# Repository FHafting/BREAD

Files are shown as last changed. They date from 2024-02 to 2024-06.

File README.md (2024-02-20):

# BREAD
This project is fully documented in the paper: Shane Oberloier, Nicholas G. Whisman, Finn Hafting, Joshua M. Pearce, Open Source Framework for a Broadly Expandable and Reconfigurable Data Acquisition and Automation Device (BREAD), ''HardwareX'', 2023, e00467, https://doi.org/10.1016/j.ohx.2023.e00467.

All case designs can be found on Onshape: https://cad.onshape.com/documents/f4c13a5c0b1f8d88ed1f5752/w/29d0c0346ddaeb06e16ff42f/e/1077373224ada363d171e3fe?renderMode=0&uiState=65d3aad45b82c32cb51ae4c9

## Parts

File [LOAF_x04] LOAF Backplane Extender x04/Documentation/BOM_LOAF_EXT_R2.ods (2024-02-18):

References | Value | Footprint | Quantity | URL
J2, J3, J4, J5 | Conn_01x10_Male | BREAD 10-Pin Connector | 4 | https://www.digikey.ca/en/products/detail/amphenol-cs-fci/10129378-910002BLF/7915958
J1 | 10129379-910002BLF | 1x10 RA Male Header 2.54mm Pitch | 1 | https://www.digikey.ca/en/products/detail/amphenol-cs-fci/10129379-910002BLF/7916010
J6 | PPPC101LGBN-RC | PinSocket_1x10_P2.54mm_Horizontal | 1 | https://www.digikey.ca/en/products/detail/sullins-connector-solutions/PPTC101LGBN-RC/775904
J7 | Barrel_Jack | BarrelJack_CUI_PJ-063AH_Horizontal | 1 | https://www.digikey.ca/en/products/detail/cui-devices/pj-063ah/2161208

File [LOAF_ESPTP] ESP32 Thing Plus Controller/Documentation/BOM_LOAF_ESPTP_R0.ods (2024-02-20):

References | Value | Footprint | Quantity | URL | Alternate
C1, C3, C4 | 22uF | C_1206_3216Metric | 3 | https://www.digikey.ca/en/products/detail/samsung-electro-mechanics/CL31A226KAHNNNE/3888705
C2 | 100nF | C_1206_3216Metric | 1 | https://www.digikey.ca/en/products/detail/samsung-electro-mechanics/CL31B104KBCNNNC/3886675
R1, R2, R3, R4, R5, R6, R7 | 10k | R_0603_1608Metric | 7 | https://www.digikey.ca/en/products/detail/stackpole-electronics-inc/RMCF0603FT10K0/1761235
R9, R11 | 4.7k | R_0603_1608Metric | 2 | https://www.digikey.ca/en/products/detail/stackpole-electronics-inc/RMCF0603FT4K70/1760998
R10, R12 | 2.2k | R_0603_1608Metric | 2 | https://www.digikey.ca/en/products/detail/yageo/RC0603JR-132K2L/14286397
R8 | 200k | R_0603_1608Metric | 1 | https://www.digikey.ca/en/products/detail/stackpole-electronics-inc/RMCF0603FT200K/1760715
L1 | 4.7uH | L_1210_3225Metric | 1 | https://www.digikey.ca/en/products/detail/tdk-corporation/BCL322520RT-4R7M-D/15849704
U1 | LTC4311ISC6-TRMPBF | SOT-363_SC-70-6 | 1 | https://www.digikey.ca/en/products/detail/analog-devices-inc/LTC4311ISC6-TRMPBF/1814493
U2 | AP63205WU-7 | TSOT-23-6 | 1 | https://www.digikey.ca/en/products/detail/diodes-incorporated/AP63205WU-7/9858424
U3 | PCA9306 | SSOP-8_2.95x2.8mm_P0.65mm | 1 | https://www.digikey.ca/en/products/detail/texas-instruments/PCA9306DCUR/768359
Q1, Q2, Q3 | BSS138 | SOT-23 | 3 | https://www.digikey.ca/en/products/detail/diodes-incorporated/BSS138-7-F/717843?productid=717843&gad_source=1
HS1 | Heatsink_Pad (optional) | Thermal Pad | 1 | https://www.digikey.ca/en/products/detail/assmann-wsw-components/V2017B/3511410
J2 | THING_PLUS_LOGICAL | ESP_THING_PLUS | 1 | https://www.sparkfun.com/products/20168 | https://www.digikey.ca/en/products/detail/sparkfun-electronics/WRL-20168/16688100
J6 | PPTC101LGBN-RC | PinSocket_1x10_P2.54mm_Horizontal | 1 | https://www.digikey.ca/en/products/detail/sullins-connector-solutions/PPTC101LGBN-RC/775904

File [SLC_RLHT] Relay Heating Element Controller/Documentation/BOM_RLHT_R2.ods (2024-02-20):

References | Value | Footprint | Quantity | URL
C1, C3, C4 | 22uF | C_1206_3216Metric | 3 | https://www.digikey.ca/en/products/detail/samsung-electro-mechanics/CL31A226KAHNNNE/3888705
C5, C6 | 0.01 uF | C_1206_3216Metric | 2 | https://www.digikey.ca/en/products/detail/walsin-technology-corporation/1206B103J500CT/9355096
C2 | 100nF | C_1206_3216Metric | 1 | https://www.digikey.ca/en/products/detail/samsung-electro-mechanics/CL31B104KBCNNNC/3886675
L1 | 4.7uH | L_1210_3225Metric | 1 | https://www.digikey.ca/en/products/detail/tdk-corporation/BCL322520RT-4R7M-D/15849704
D2, D3 | General_Purpose_Diode | D_DO-35_SOD27_P7.62mm_Horizontal | 2 | https://www.digikey.ca/en/products/detail/onsemi/1N914B/978757
D1 | WS2812B_5050 | WS2812-5050-4PIN | 1 | https://www.digikey.ca/en/products/detail/sparkfun-electronics/COM-16347/11630204
U2, U5 | TCMT1100 | SOP-4_4.4x2.6mm_P1.27mm | 2 | https://www.digikey.ca/en/products/detail/vishay-semiconductor-opto-division/TCMT1100/1738630
U3, U4 | MAX6675ISA+ | SOIC127P600X175-8N | 2 | https://www.digikey.ca/en/products/detail/maxim-integrated/MAX6675ISA/1513517
U1 | AP63205WU-7 | TSOT-23-6 | 1 | https://www.digikey.ca/en/products/detail/diodes-incorporated/AP63205WU-7/9858424
F1, F2 | 10A | Glass Fuse Clip x2 (5x20MM) | 4 | https://www.digikey.ca/en/products/detail/bel-fuse-inc/FC-211-BRIGHT-TIN/622587
A1 | Arduino_Nano_v3.x | Arduino_Nano | 1 | https://www.amazon.ca/ELEGOO-Arduino-ATmega328P-Without-Compatible/dp/B0713XK923
FB1, FB2, FB3, FB4 | Ferrite_Bead_Small | R_1206_3216Metric | 4 | https://www.digikey.ca/en/products/detail/w%C3%BCrth-elektronik/74279215/1639033
K1, K2 | G5Q-1 | Relay_SPDT_Omron-G5Q-1 | 2 | https://www.digikey.ca/en/products/detail/omron-electronics-inc-emc-div/G5Q-14-DC12/355243
HS1 | Heatsink_Pad (optional) | Thermal Pad | 1 | https://www.digikey.ca/en/products/detail/assmann-wsw-components/V2017B/3511410
J4 | Term_PressFit_Phoenix_Contact | Term_PressFit_3.5mm_H_ENDCAP_PC | 1 (4x) | https://www.digikey.ca/en/products/detail/phoenix-contact/1990753/2527254
J3, J11, J12 | Term_PressFit_Phoenix_Contact | Term_PressFit_3.5mm_H_PC
J1 | Conn_01x10_Female | PinSocket_1x10_P2.54mm_Horizontal | 1 | https://www.digikey.ca/en/products/detail/sullins-connector-solutions/PPTC101LGBN-RC/775904
J2 | I2C_01x04 | JST_SH_SM04B-SRSS-TB_1x04-1MP_P1.00mm_Horizontal | 1 | https://www.digikey.ca/en/products/detail/jst-sales-america-inc/SM04B-SRSS-TB/926710
J6, J7, J8, J9, J10, J13, J14, J15, J16, J17, J18 | Term_PressFit_Phoenix_Contact | Term_PressFit_5mm_H_PC_HVRELAY | 2 (6x) | https://www.digikey.ca/en/products/detail/phoenix-contact/1991011/2527265
J5 | Term_PressFit_Phoenix_Contact | Term_PressFit_5mm_H_ENDCAP_PC_HVRELAY
 | 10A | Glass Fuse 5x20mm | 2 | https://www.digikey.ca/en/products/detail/bel-fuse-inc/5ST-10-R/1009028

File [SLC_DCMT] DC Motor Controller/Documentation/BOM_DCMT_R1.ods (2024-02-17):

References | Value | Footprint | Quantity | URL
C6, C8, C9, C10, C11, C12 | 10 nF | C_1206_3216Metric_Pad1.33x1.80mm_HandSolder | 6 | https://www.digikey.ca/en/products/detail/walsin-technology-corporation/1206B103J500CT/9355096
C1, C5, C7 | 22uF | C_1206_3216Metric | 3 | https://www.digikey.ca/en/products/detail/samsung-electro-mechanics/CL31A226KAHNNNE/3888705
C2, C3 | 10uF_t | C_1206_3216Metric | 2 | https://www.digikey.ca/en/products/detail/yageo/cc1206kkx5r8bb106/2833631
C4 | 100nF | C_1206_3216Metric | 1 | https://www.digikey.ca/en/products/detail/samsung-electro-mechanics/CL31B104KBCNNNC/3886675
R1, R2 | 4.42 k | R_1206_3216Metric_Pad1.30x1.75mm_HandSolder | 2 | https://www.digikey.ca/en/products/detail/yageo/RC1206FR-074K42L/728878
L1 | 4.7uH | L_1210_3225Metric | 1 | https://www.digikey.ca/en/products/detail/tdk-corporation/BCL322520RT-4R7M-D/15849704
D2 | WS2812B_5050 | WS2812-5050-4PIN | 1 | https://www.digikey.ca/en/products/detail/sparkfun-electronics/COM-16347/11630204
U1, U3 | LMD18200 | TO-220-11_P3.4x5.08mm_StaggerOdd_Lead4.85mm_Vertical | 2 | https://www.digikey.ca/en/products/detail/texas-instruments/LMD18200T/3701191
U2 | AP63205WU-7 | TSOT-23-6 | 1 | https://www.digikey.ca/en/products/detail/diodes-incorporated/AP63205WU-7/9858424
SW1, SW2 | SW_SPDT | L102011MS02Q | 2 | https://www.digikey.ca/en/products/detail/c-k/L102011MS02Q/484143
A1 | Arduino_Nano_v3.x | Arduino_Nano | 1 | https://www.amazon.ca/ELEGOO-Arduino-ATmega328P-Without-Compatible/dp/B0713XK923
HS1 | Heatsink_Pad (optional) | Thermal Pad | 1 | https://www.digikey.ca/en/products/detail/assmann-wsw-components/V2017B/3511410
J10, J11, J13, J15, J16, J17 | Term_PressFit_Phoenix_Contact | Term_PressFit_5mm_H_PC | 2 (4x) | https://www.digikey.ca/en/products/detail/phoenix-contact/1990999/3605138
J12, J14 | Term_PressFit_Phoenix_Contact | Term_PressFit_5mm_H_ENDCAP_PC
J2, J3, J4, J5, J7, J8, J9 | Term_PressFit_Phoenix_Contact | Term_PressFit_3.5mm_H_PC | 1 (8x) | https://www.digikey.ca/en/products/detail/phoenix-contact/1990795/3605145
J6 | Term_PressFit_Phoenix_Contact | Term_PressFit_3.5mm_H_ENDCAP_PC | 1
J1 | Conn_01x10_Female | PinSocket_1x10_P2.54mm_Horizontal | 1 | https://www.digikey.ca/en/products/detail/sullins-connector-solutions/PPTC101LGBN-RC/775904
J18 | I2C_01x04 | JST_SH_SM04B-SRSS-TB_1x04-1MP_P1.00mm_Horizontal | 1 | https://www.digikey.ca/en/products/detail/jst-sales-america-inc/SM04B-SRSS-TB/926710

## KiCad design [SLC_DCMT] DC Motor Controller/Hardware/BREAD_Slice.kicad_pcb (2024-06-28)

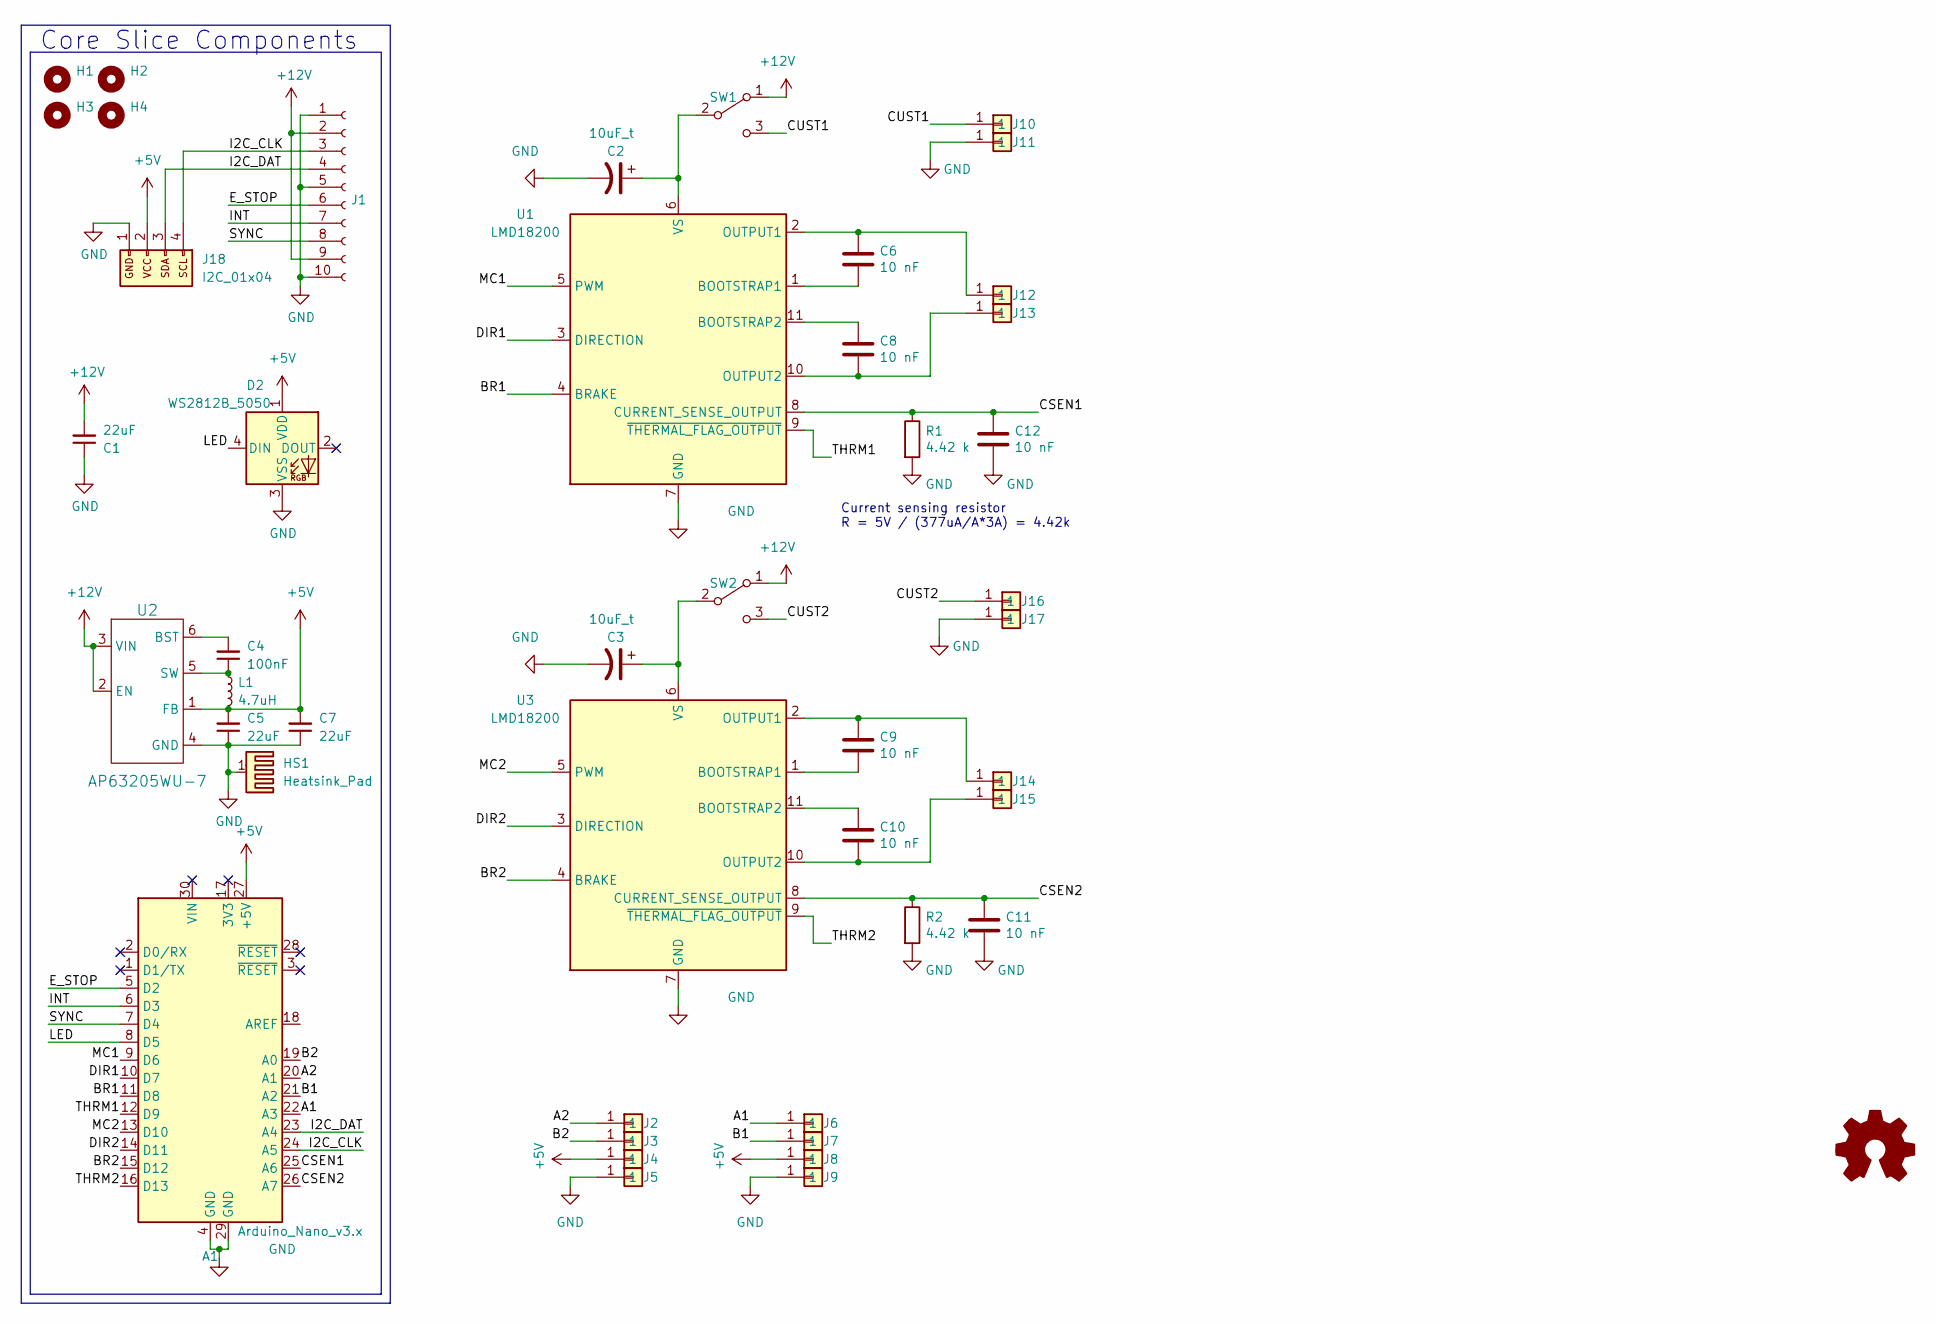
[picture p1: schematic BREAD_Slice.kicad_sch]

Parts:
A1: Arduino_Nano_v3.x; Arduino_Nano
C1, C5, C7: 22uF; C_1206_3216Metric
C2, C3: 10uF_t; C_1206_3216Metric; Part # T491C106K025AT
C4: 100nF; C_1206_3216Metric
C6, C8, C9, C10, C11, C12: 10 nF; C_1206_3216Metric_Pad1.33x1.80mm_HandSolder
D2: WS2812B_5050; WS2812-5050-4PIN
H1, H2, H3, H4: MountingHole; MountingHole_5mm
HS1: Heatsink_Pad; Thermal Pad
J1: Conn_01x10_Female; PinSocket_1x10_P2.54mm_Horizontal
J2, J3, J4, J5, J7, J8, J9: Term_PressFit_Phoenix_Contact; Term_PressFit_3.5mm_H_PC
J6: Term_PressFit_Phoenix_Contact; Term_PressFit_3.5mm_H_ENDCAP_PC
J10, J11, J13, J15, J16, J17: Term_PressFit_Phoenix_Contact; Term_PressFit_5mm_H_PC
J12, J14: Term_PressFit_Phoenix_Contact; Term_PressFit_5mm_H_ENDCAP_PC
J18: I2C_01x04; JST_SH_SM04B-SRSS-TB_1x04-1MP_P1.00mm_Horizontal
L1: 4.7uH; L_1210_3225Metric
Logo1: Logo_Open_Hardware_Small; OSHW-Symbol_6.7x6mm_SilkScreen
R1, R2: 4.42 k; R_1206_3216Metric_Pad1.30x1.75mm_HandSolder
SW1, SW2: SW_SPDT; L102011MS02Q
U1, U3: LMD18200; TO-220-11_P3.4x5.08mm_StaggerOdd_Lead4.85mm_Vertical
U2: AP63205WU-7; TSOT-23-6

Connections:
+5V: A1.27 (+5V), C5.2, C7.2, D2.1 (VDD), J4.1, J8.1, J18.2, L1.2, U2.1 (FB)
+12V: C1.2, J1.2, J1.9, SW1.1 (A), SW2.1 (A), U2.2 (EN), U2.3 (VIN)
/A1: A1.22 (A3), J6.1
/A2: A1.20 (A1), J2.1
/B1: A1.21 (A2), J7.1
/B2: A1.19 (A0), J3.1
/BR1: A1.11 (D8), U1.4 (BRAKE)
/BR2: A1.15 (D12), U3.4 (BRAKE)
/CSEN1: A1.25 (A6), C12.1, R1.1, U1.8 (CURRENT_SENSE_OUTPUT)
/CSEN2: A1.26 (A7), C11.1, R2.1, U3.8 (CURRENT_SENSE_OUTPUT)
/CUST1: J10.1, SW1.3 (C)
/CUST2: J16.1, SW2.3 (C)
/DIR1: A1.10 (D7), U1.3 (DIRECTION)
/DIR2: A1.14 (D11), U3.3 (DIRECTION)
/E_STOP: A1.5 (D2), J1.6
/I2C_CLK: A1.24 (A5), J1.3, J18.4
/I2C_DAT: A1.23 (A4), J1.4, J18.3
/INT: A1.6 (D3), J1.7
/LED: A1.8 (D5), D2.4 (DIN)
/MC1: A1.9 (D6), U1.5 (PWM)
/MC2: A1.13 (D10), U3.5 (PWM)
/SYNC: A1.7 (D4), J1.8
/THRM1: A1.12 (D9), U1.9 (~THERMAL_FLAG_OUTPUT)
/THRM2: A1.16 (D13), U3.9 (~THERMAL_FLAG_OUTPUT)
GND: A1.4 (GND), A1.29 (GND), C1.1, C2.2, C3.2, C5.1, C7.1, C11.2, C12.2, D2.3 (VSS), HS1.1, J1.1, J1.5, J1.10, J5.1, J9.1, J11.1, J17.1, J18.1, R1.2, R2.2, U1.7 (GND), U2.4 (GND), U3.7 (GND)
unnamed: C2.1, SW1.2 (B), U1.6 (VS)
unnamed: C3.1, SW2.2 (B), U3.6 (VS)
unnamed: C6.2, U1.1 (BOOTSTRAP1)
unnamed: C8.1, U1.11 (BOOTSTRAP2)
unnamed: C6.1, J12.1, U1.2 (OUTPUT1)
unnamed: C8.2, J13.1, U1.10 (OUTPUT2)
unnamed: C4.2, U2.6 (BST)
unnamed: C4.1, L1.1, U2.5 (SW)
unnamed: C9.2, U3.1 (BOOTSTRAP1)
unnamed: C10.1, U3.11 (BOOTSTRAP2)
unnamed: C9.1, J14.1, U3.2 (OUTPUT1)
unnamed: C10.2, J15.1, U3.10 (OUTPUT2)

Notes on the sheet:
Current sensing resistor R = 5V / (377uA/A*3A) = 4.42k
Core Slice Components

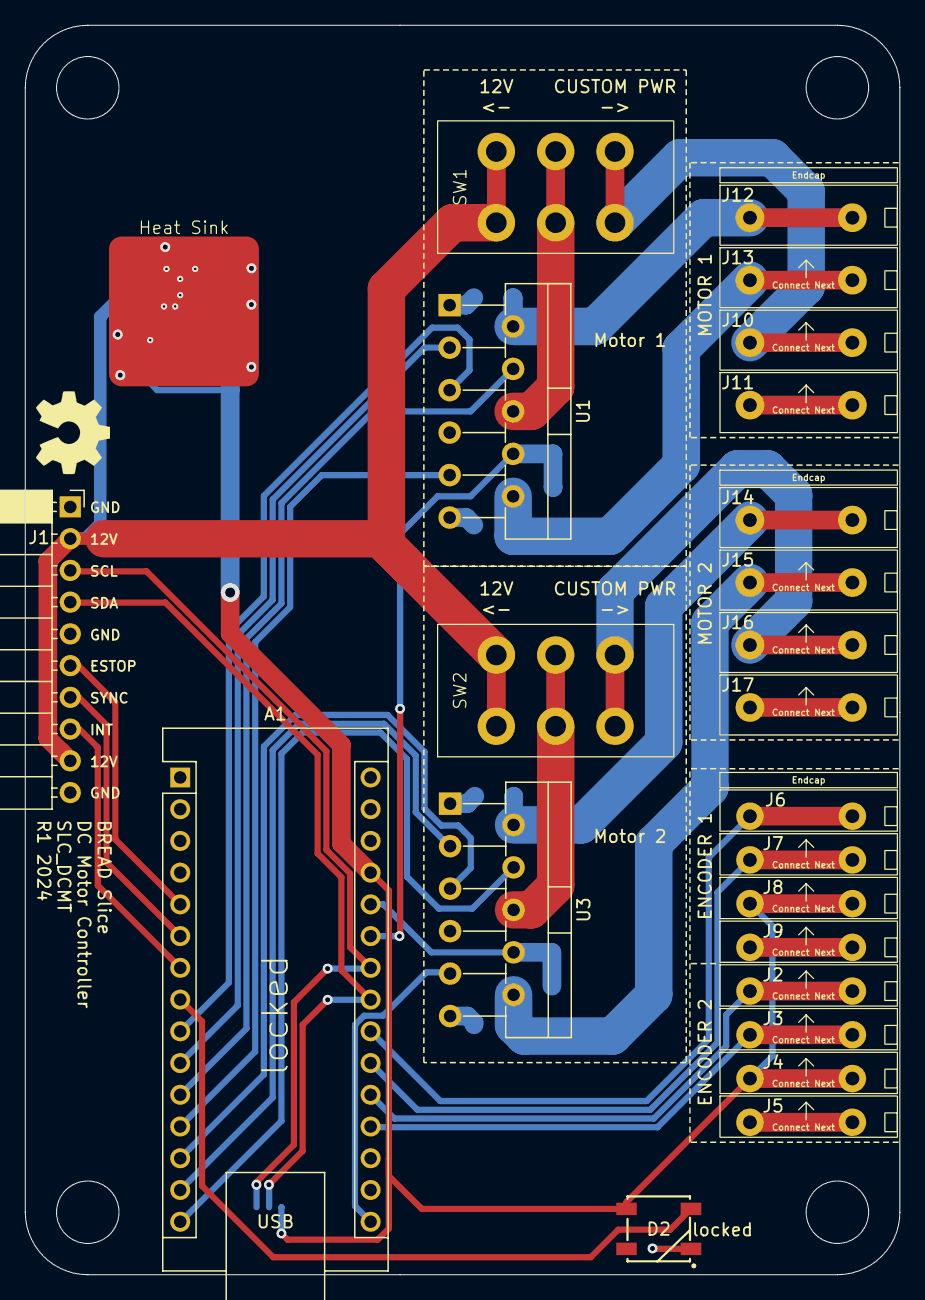
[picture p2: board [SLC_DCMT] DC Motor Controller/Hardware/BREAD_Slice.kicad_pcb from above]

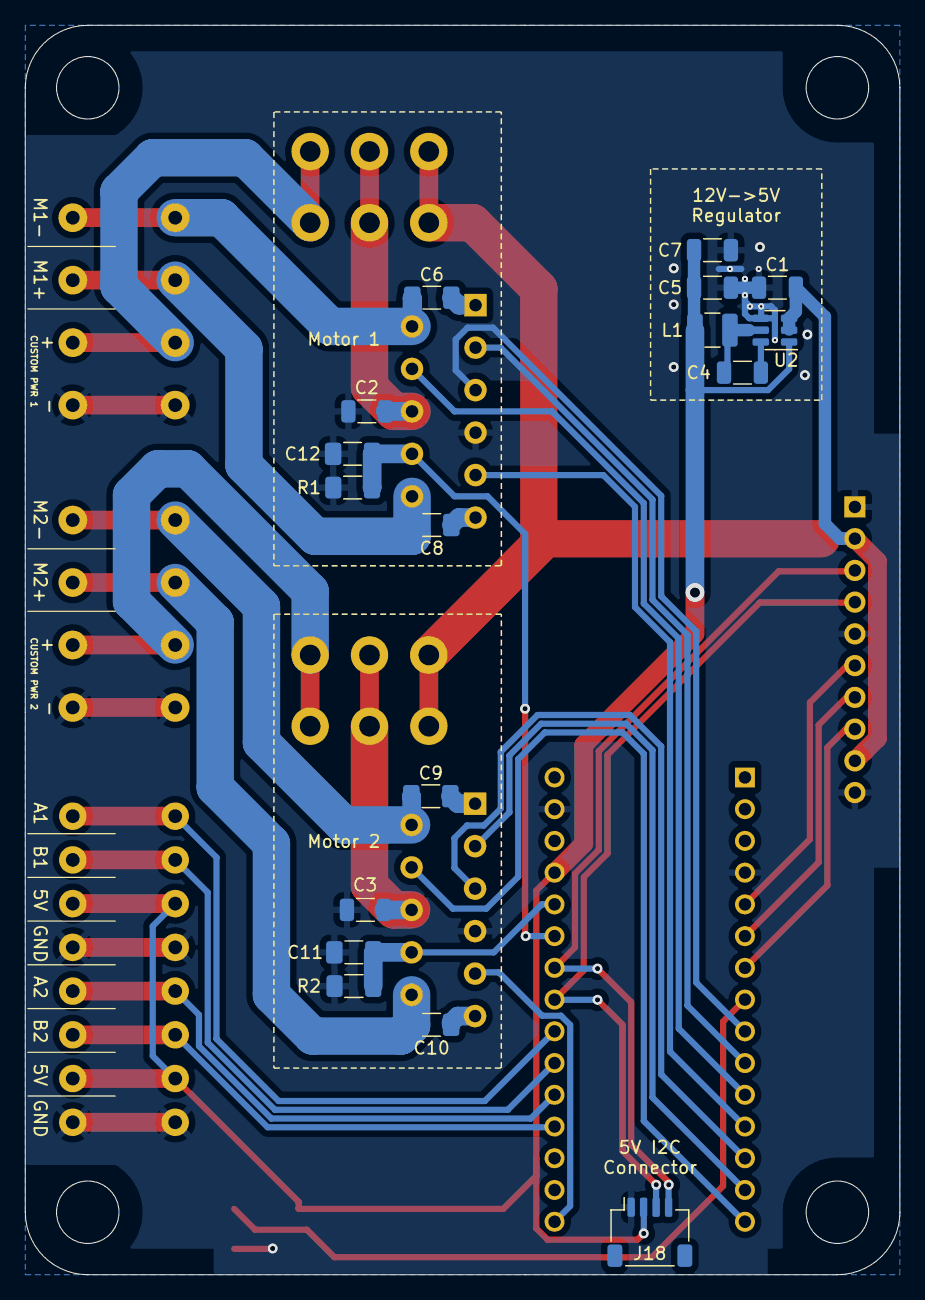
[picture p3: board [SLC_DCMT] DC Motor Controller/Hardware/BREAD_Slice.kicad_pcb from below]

Board: 2 copper layers, 70.0 x 100.0 mm, 46 parts (17 on the bottom side), 37 nets.

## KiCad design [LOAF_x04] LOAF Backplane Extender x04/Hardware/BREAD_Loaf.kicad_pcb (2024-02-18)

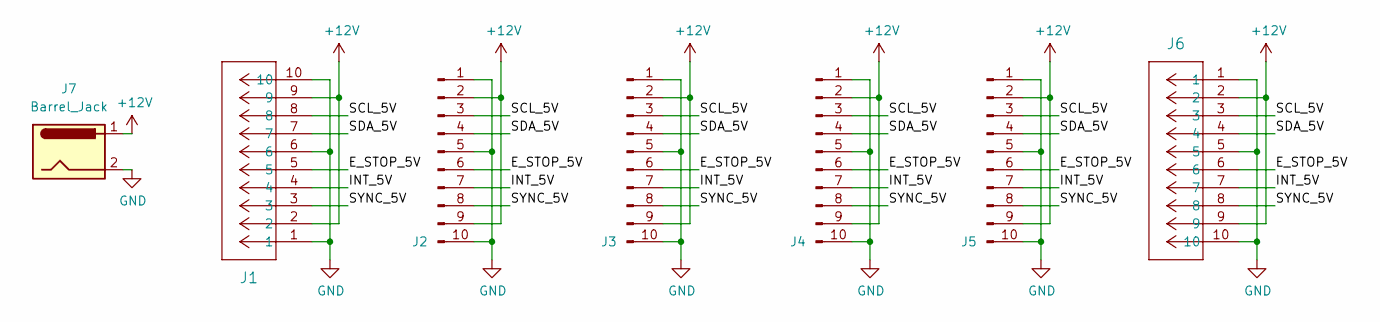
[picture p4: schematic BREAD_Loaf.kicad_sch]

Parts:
J1: PPPC101LGBN-RC; 1x10 RA Male Header 2.54mm Pitch
J2, J3, J4, J5: Conn_01x10_Male; BREAD 10-Pin Connector
J6: PPPC101LGBN-RC; PinSocket_1x10_P2.54mm_Horizontal
J7: Barrel_Jack; BarrelJack_CUI_PJ-063AH_Horizontal

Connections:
+12V: J1.2, J1.9, J2.2, J2.9, J3.2, J3.9, J4.2, J4.9, J5.2, J5.9, J6.2, J6.9, J7.1
/E_STOP_5V: J1.5, J2.6, J3.6, J4.6, J5.6, J6.6
/INT_5V: J1.4, J2.7, J3.7, J4.7, J5.7, J6.7
/SCL_5V: J1.8, J2.3, J3.3, J4.3, J5.3, J6.3
/SDA_5V: J1.7, J2.4, J3.4, J4.4, J5.4, J6.4
/SYNC_5V: J1.3, J2.8, J3.8, J4.8, J5.8, J6.8
GND: J1.1, J1.6, J1.10, J2.1, J2.5, J2.10, J3.1, J3.5, J3.10, J4.1, J4.5, J4.10, J5.1, J5.5, J5.10, J6.1, J6.5, J6.10, J7.2

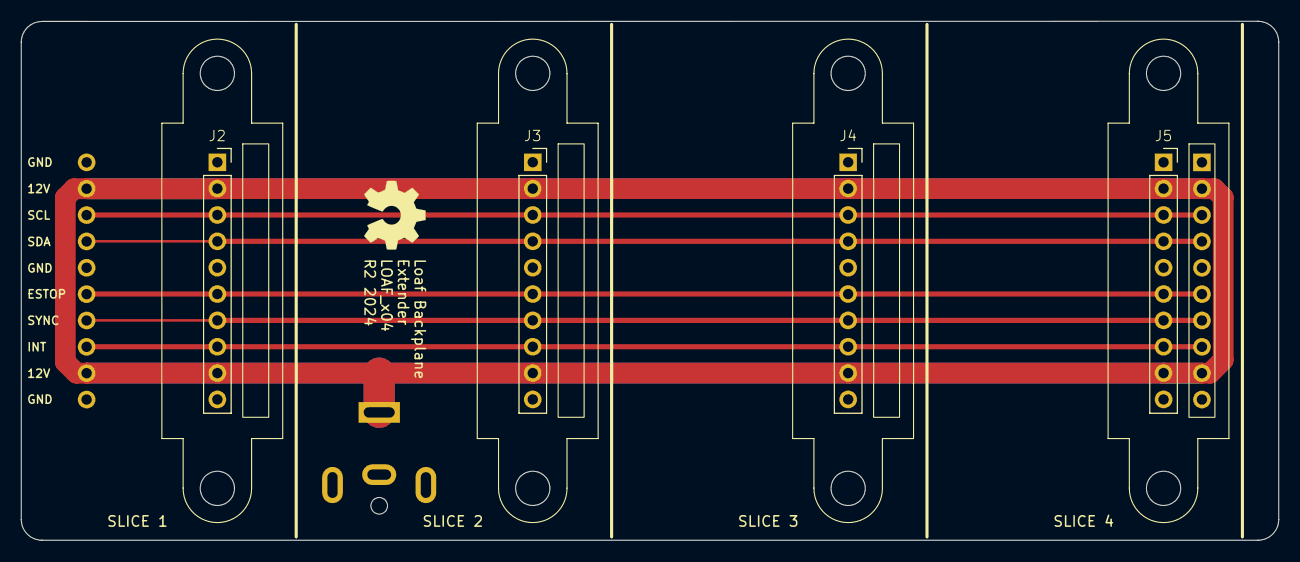
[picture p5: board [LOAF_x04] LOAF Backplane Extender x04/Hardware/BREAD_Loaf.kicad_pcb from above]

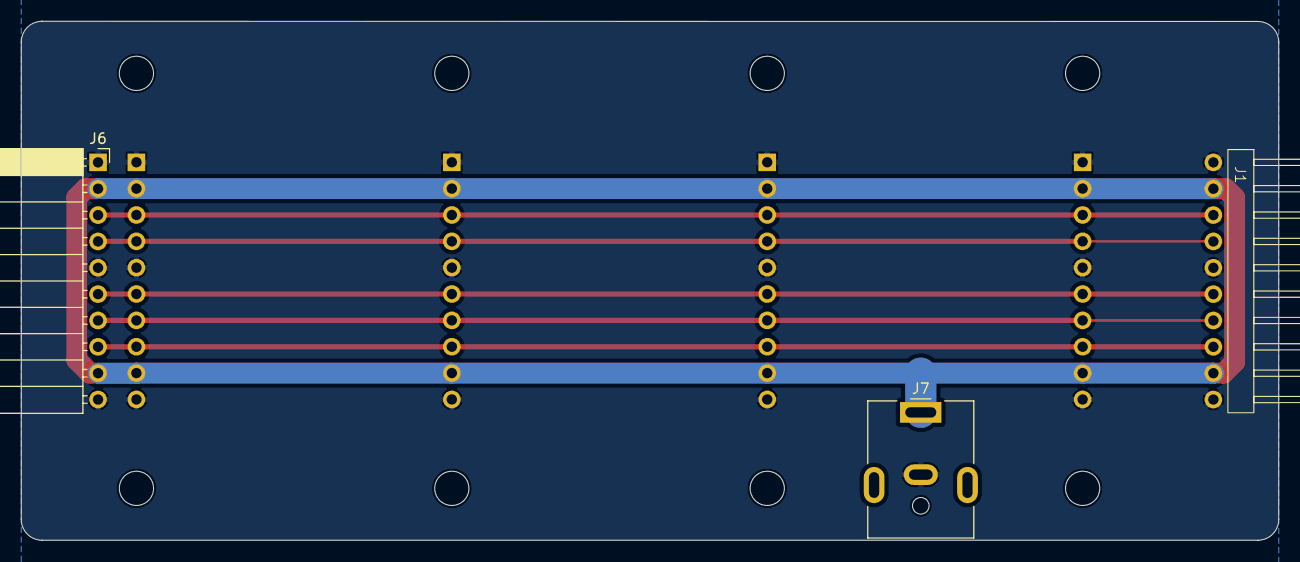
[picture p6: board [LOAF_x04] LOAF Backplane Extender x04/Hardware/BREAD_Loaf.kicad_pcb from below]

Board: 2 copper layers, 121.2 x 50.0 mm, 8 parts (3 on the bottom side), 7 nets.

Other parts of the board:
Logo1: Logo_Open_Hardware_Small; OSHW-Symbol_6.7x6mm_SilkScreen

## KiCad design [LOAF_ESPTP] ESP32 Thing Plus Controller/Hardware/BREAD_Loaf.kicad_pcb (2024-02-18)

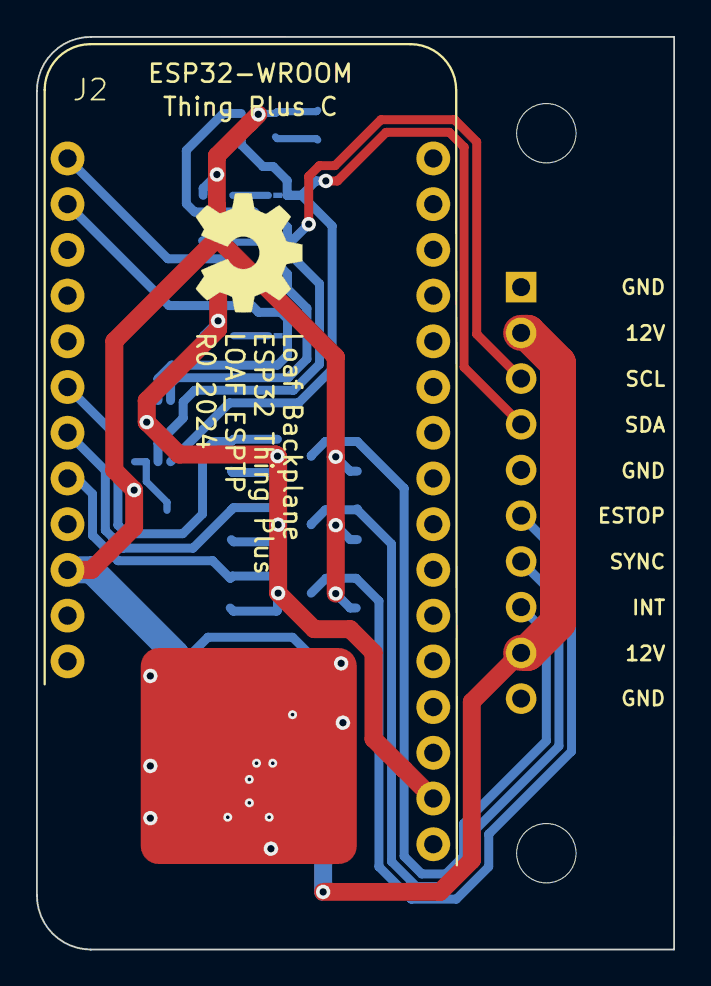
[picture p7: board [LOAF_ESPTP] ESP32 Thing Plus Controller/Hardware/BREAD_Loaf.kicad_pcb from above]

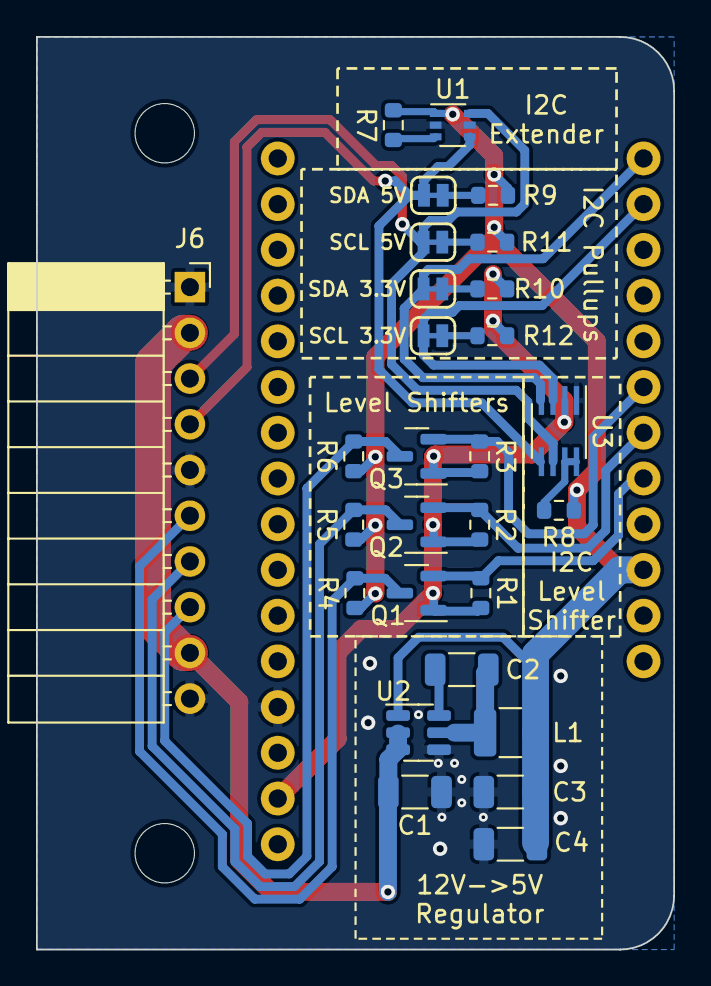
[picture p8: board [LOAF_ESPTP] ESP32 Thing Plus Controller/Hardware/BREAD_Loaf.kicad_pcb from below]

Board: 2 copper layers, 35.4 x 50.7 mm, 33 parts (28 on the bottom side), 22 nets.

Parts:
C1, C3, C4: 22uF; C_1206_3216Metric
C2: 100nF; C_1206_3216Metric
HS1: Heatsink_Pad; Thermal Pad
J2: THING_PLUS_LOGICAL; ESP_THING_PLUS
J6: PPPC101LGBN-RC; PinSocket_1x10_P2.54mm_Horizontal
JP1, JP2, JP3, JP4: SMT-JUMPER_2_NC_TRACE_SILK
L1: 4.7uH; L_1210_3225Metric
Logo1: Logo_Open_Hardware_Small; OSHW-Symbol_6.7x6mm_SilkScreen
Q1, Q2, Q3: BSS138; SOT-23
R1, R2, R3, R4, R5, R6, R7: 10k; R_0603_1608Metric
R8: 200k; R_0603_1608Metric
R9, R11: 4.7k; R_0603_1608Metric
R10, R12: 2.2k; R_0603_1608Metric
ST1, ST2: Stand_off; STAND-OFF
U1: LTC4311ISC6-TRMPBF; SOT-363_SC-70-6
U2: AP63205WU-7; TSOT-23-6
U3: PCA9306; SSOP-8_2.95x2.8mm_P0.65mm

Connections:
+3.3V: J2.27 (3.3V), Q1.1 (G), Q2.1 (G), Q3.1 (G), R1.2, R2.2, R3.2, R10.1, R12.1, U3.2 (VREF1)
+5V: C3.2, C4.2, J2.10 (V_USB), L1.2, R4.2, R5.2, R6.2, R7.1, R8.2, R9.1, R11.1, U1.1 (VCC), U2.1 (FB)
+12V: C1.2, J6.2, J6.9, U2.2 (EN), U2.3 (VIN)
/E_STOP_3.3V: J2.8 (GPIO1), Q1.2 (S), R1.1
/E_STOP_5V: J6.6, Q1.3 (D), R4.1
/INT_3.3V: J2.7 (GPIO2), Q2.2 (S), R2.1
/INT_5V: J6.7, Q2.3 (D), R5.1
/SCL_3.3V: J2.2 (SCL), JP4.2 (B), U3.3 (SCL1)
/SCL_5V: J6.3, JP2.2 (B), U1.6 (BUS1), U3.6 (SCL2)
/SDA_3.3V: J2.1 (SDA), JP3.2 (B), U3.4 (SDA1)
/SDA_5V: J6.4, JP1.2 (B), U1.4 (BUS2), U3.5 (SDA2)
/SYNC_3.3V: J2.6 (GPIO3), Q3.2 (S), R3.1
/SYNC_5V: J6.8, Q3.3 (D), R6.1
GND: C1.1, C3.1, C4.1, HS1.1, J2.25 (GND), J6.1, J6.5, J6.10, U1.2 (GND), U1.5 (GND), U2.4 (GND), U3.1 (GND)
unnamed: JP1.1 (A), R9.2
unnamed: JP2.1 (A), R11.2
unnamed: JP3.1 (A), R10.2
unnamed: JP4.1 (A), R12.2
unnamed: R7.2, U1.3 (ENABLE)
unnamed: C2.2, U2.6 (BST)
unnamed: C2.1, L1.1, U2.5 (SW)
unnamed: R8.1, U3.7 (VREF2), U3.8 (EN)

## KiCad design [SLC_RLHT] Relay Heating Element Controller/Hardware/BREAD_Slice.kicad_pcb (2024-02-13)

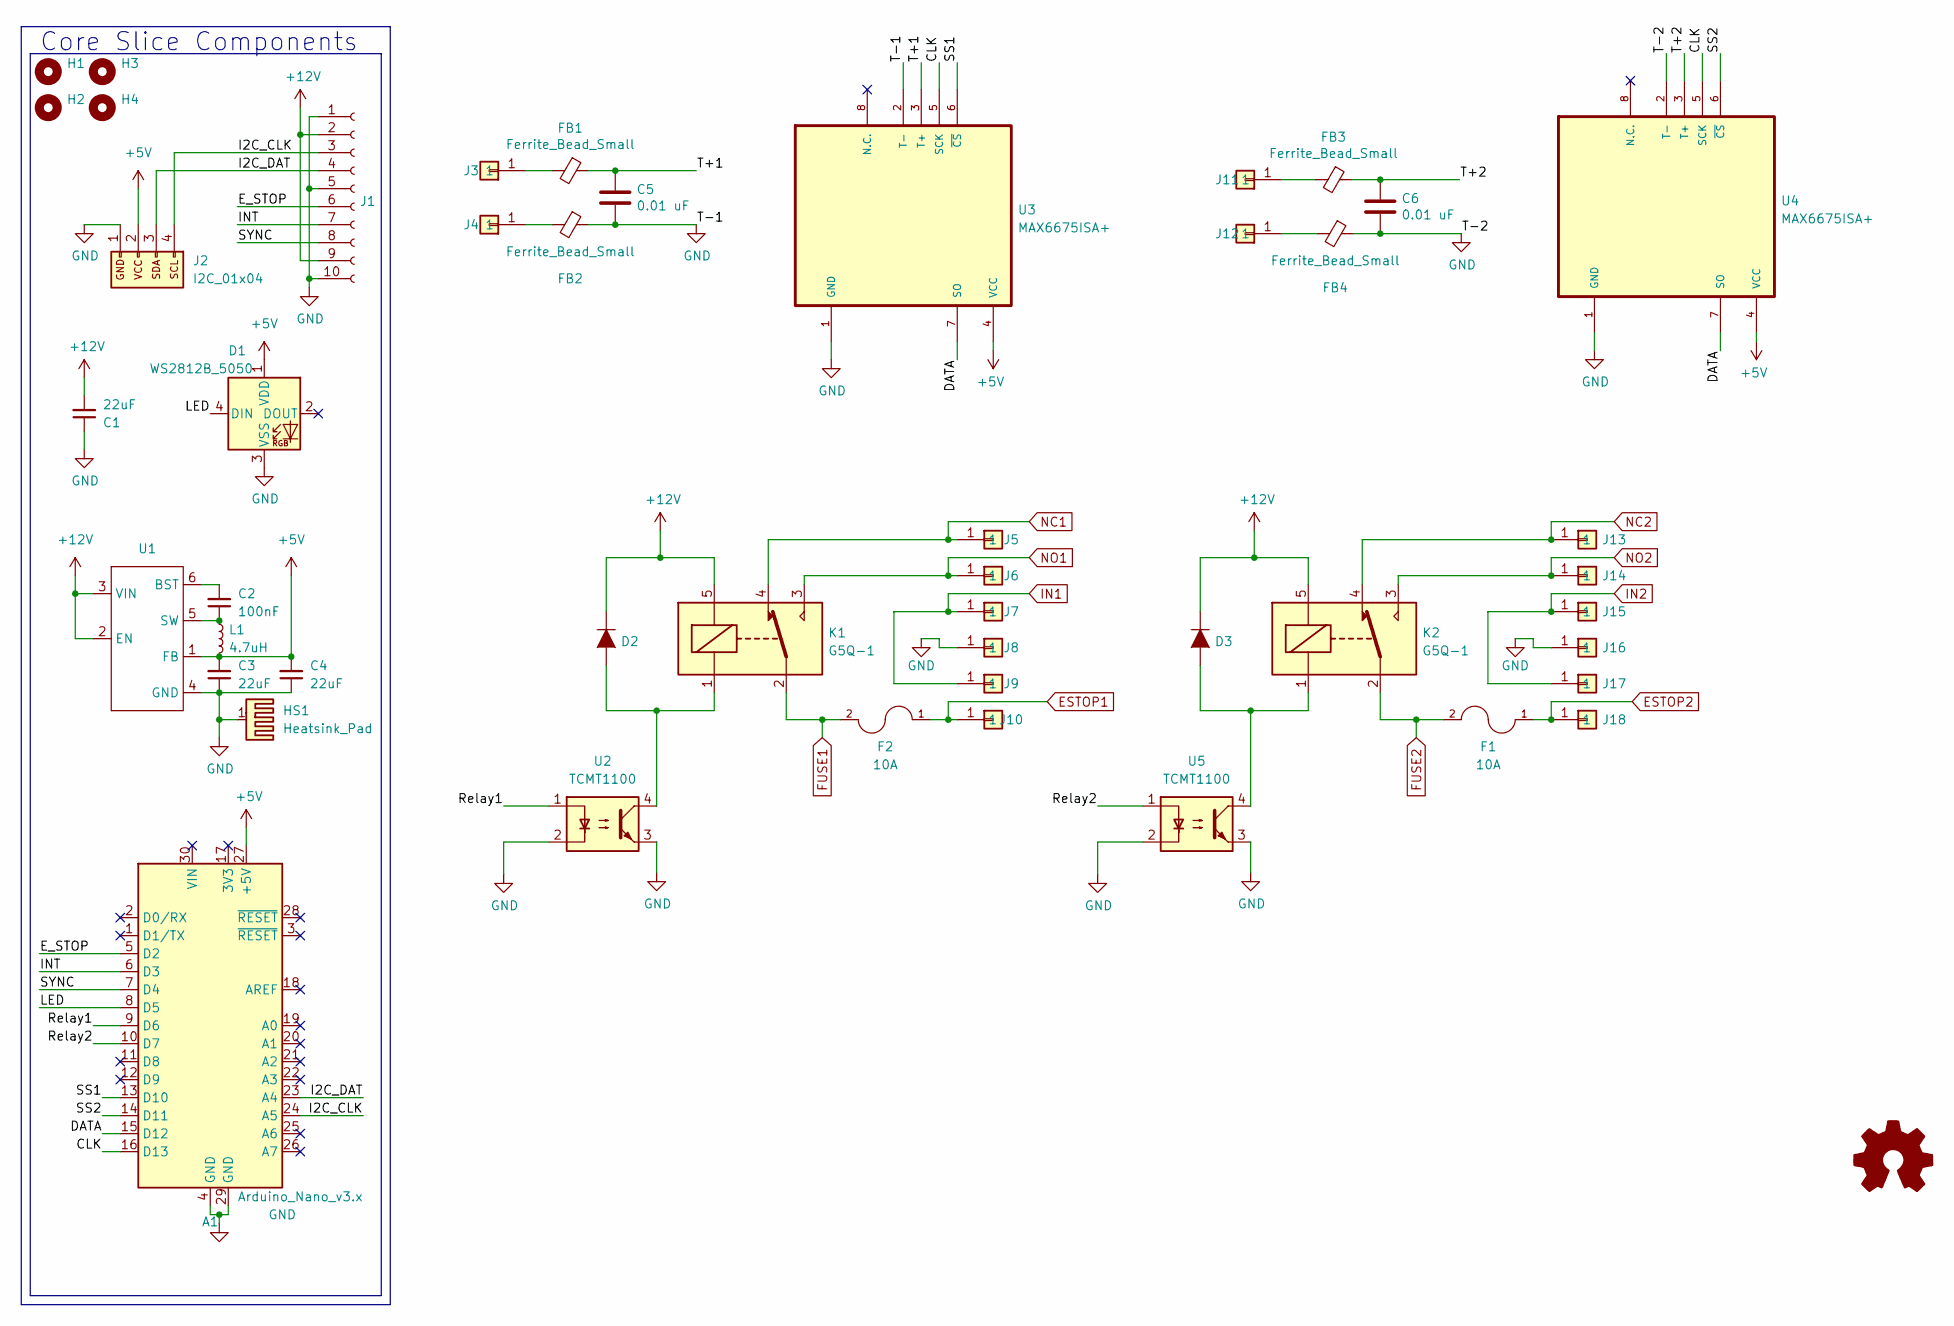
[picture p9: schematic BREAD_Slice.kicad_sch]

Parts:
A1: Arduino_Nano_v3.x; Arduino_Nano
C1, C3, C4: 22uF; C_1206_3216Metric
C2: 100nF; C_1206_3216Metric
C5, C6: 0.01 uF; C_1206_3216Metric
D1: WS2812B_5050; WS2812-5050-4PIN
D2, D3: General_Purpose_Diode; D_DO-35_SOD27_P7.62mm_Horizontal; Part # 1N914BWS
F1, F2: 10A; Glass Fuse Clip 5x20MM; Part # 3522-2
FB1, FB2, FB3, FB4: Ferrite_Bead_Small; R_1206_3216Metric
H1, H2, H3, H4: MountingHole; MountingHole_5mm
HS1: Heatsink_Pad; Thermal Pad
J1: Conn_01x10_Female; PinSocket_1x10_P2.54mm_Horizontal
J2: I2C_01x04; JST_SH_SM04B-SRSS-TB_1x04-1MP_P1.00mm_Horizontal
J3, J11, J12: Term_PressFit_Phoenix_Contact; Term_PressFit_3.5mm_H_PC
J4: Term_PressFit_Phoenix_Contact; Term_PressFit_3.5mm_H_ENDCAP_PC
J5: Term_PressFit_Phoenix_Contact; Term_PressFit_5mm_H_ENDCAP_PC_HVRELAY
J6, J7, J8, J9, J10, J13, J14, J15, J16, J17, J18: Term_PressFit_Phoenix_Contact; Term_PressFit_5mm_H_PC_HVRELAY
K1, K2: G5Q-1; Relay_SPDT_Omron-G5Q-1
L1: 4.7uH; L_1210_3225Metric
U1: TSOT-23-6
U2, U5: TCMT1100; SOP-4_4.4x2.6mm_P1.27mm
U3, U4: MAX6675ISA+; SOIC127P600X175-8N

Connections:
+5V: A1.27 (+5V), C3.2, C4.2, D1.1 (VDD), J2.2, L1.2, U1.1 (FB), U3.4 (VCC), U4.4 (VCC)
+12V: C1.2, D2.1 (K), D3.1 (K), J1.2, J1.9, K1.5, K2.5, U1.2 (EN), U1.3 (VIN)
/CLK: A1.16 (D13), U3.5 (SCK), U4.5 (SCK)
/DATA: A1.15 (D12), U3.7 (SO), U4.7 (SO)
/E_STOP: A1.5 (D2), J1.6
/I2C_CLK: A1.24 (A5), J1.3, J2.4
/I2C_DAT: A1.23 (A4), J1.4, J2.3
/INT: A1.6 (D3), J1.7
/LED: A1.8 (D5), D1.4 (DIN)
/Relay1: A1.9 (D6), U2.1
/Relay2: A1.10 (D7), U5.1
/SS1: A1.13 (D10), U3.6 (~CS)
/SS2: A1.14 (D11), U4.6 (~CS)
/SYNC: A1.7 (D4), J1.8
/T+1: C5.1, FB1.1, U3.3 (T+)
/T+2: C6.1, FB3.1, U4.3 (T+)
ESTOP1: F2.1, J10.1
ESTOP2: F1.1, J18.1
FUSE1: F2.2, K1.2
FUSE2: F1.2, K2.2
GND: A1.4 (GND), A1.29 (GND), C1.1, C3.1, C4.1, C5.2, C6.2, D1.3 (VSS), FB2.1, FB4.1, HS1.1, J1.1, J1.5, J1.10, J2.1, J8.1, J16.1, U1.4 (GND), U2.2, U2.3, U3.1 (GND), U3.2 (T-), U4.1 (GND), U4.2 (T-), U5.2, U5.3
IN1: J7.1, J9.1
IN2: J15.1, J17.1
NC1: J5.1, K1.4
NC2: J13.1, K2.4
NO1: J6.1, K1.3
NO2: J14.1, K2.3
unnamed: D2.2 (A), K1.1, U2.4
unnamed: D3.2 (A), K2.1, U5.4
unnamed: FB1.2, J3.1
unnamed: FB2.2, J4.1
unnamed: FB3.2, J11.1
unnamed: FB4.2, J12.1
unnamed: C2.2, U1.6 (BST)
unnamed: C2.1, L1.1, U1.5 (SW)

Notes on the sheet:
Core Slice Components

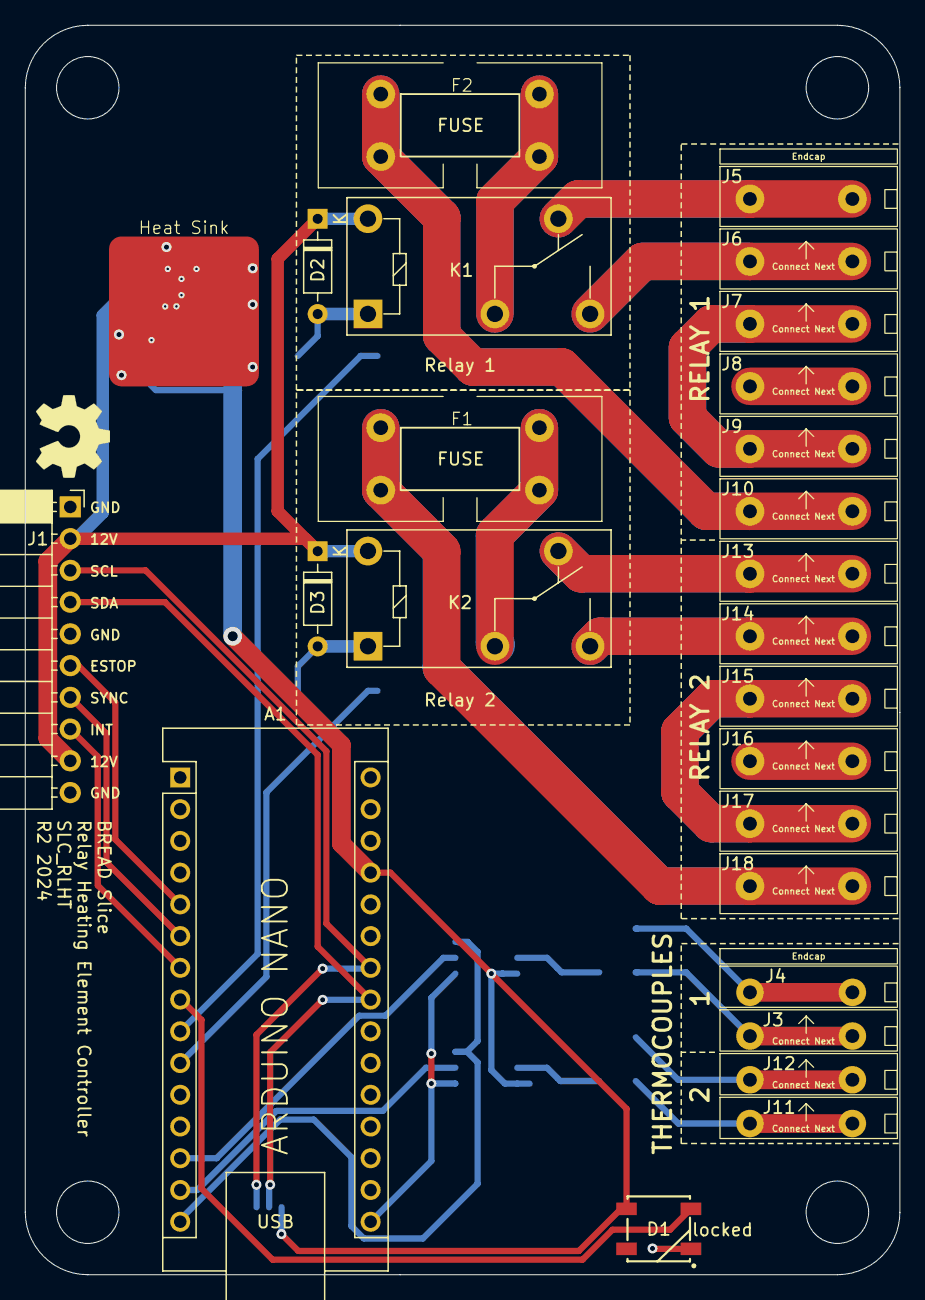
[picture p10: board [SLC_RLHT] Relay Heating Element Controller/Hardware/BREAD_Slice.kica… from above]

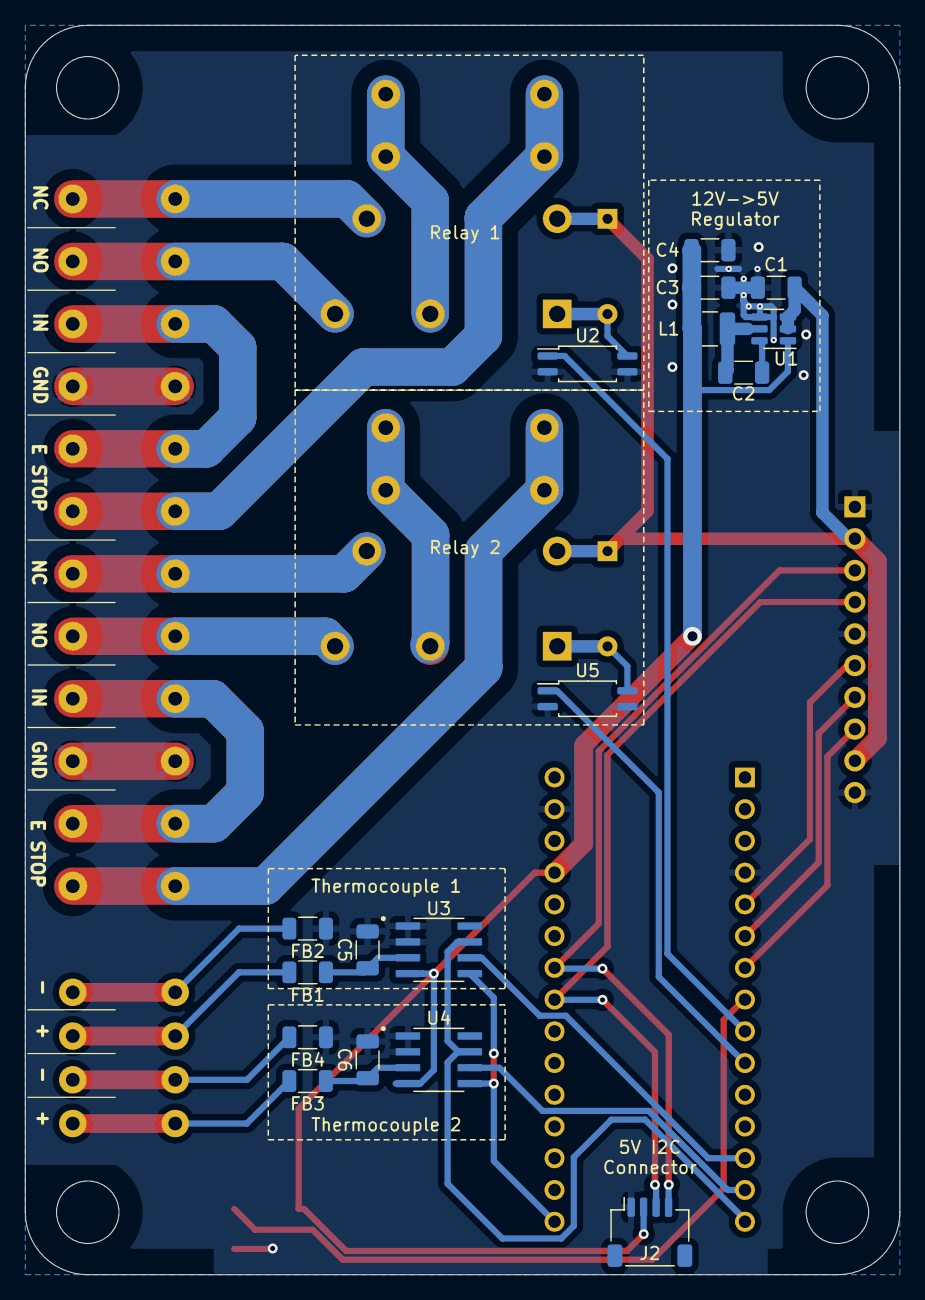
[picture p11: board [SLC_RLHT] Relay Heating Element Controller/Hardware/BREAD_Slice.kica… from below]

Board: 2 copper layers, 70.0 x 100.0 mm, 48 parts (17 on the bottom side), 35 nets.

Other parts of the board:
Logo1: Logo_Open_Hardware_Small; OSHW-Symbol_6.7x6mm_SilkScreen

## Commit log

2024-02-13 Added SLC_RLHT R1 hardware files
    [BREAD_Slice-B_Cu.gbr, BREAD_Slice-B_Mask.gbr, BREAD_Slice-B_Paste.gbr, BREAD_Slice-B_Silkscreen.gbr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]
2024-02-16 Added BOM for RLHT_R2
    [BOM_RLHT_R2.ods]
2024-02-17 Updated RLHT BOM
    [BOM_RLHT_R2.ods]
2024-02-17 Added SLC_DCMT_R1 files
    [BOM_DCMT_R1.ods, BREAD_Slice-B_Cu.gbr, BREAD_Slice-B_Mask.gbr, BREAD_Slice-B_Paste.gbr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]
2024-02-18 Added LOAF_ESPTP_R0 files
    [BOM_LOAF_ESPTP_R0.ods, BREAD_Loaf-B_Cu.gbr, BREAD_Loaf-B_Mask.gbr, BREAD_Loaf-B_Paste.gbr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]
2024-02-18 Added LOAF_x04_R2 files
    [BOM_LOAF_EXT_R2.ods, BREAD_Loaf-B_Cu.gbr, BREAD_Loaf-B_Mask.gbr, BREAD_Loaf-B_Paste.gbr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]
2024-02-20 Updated BOM for ESPTP and RLHT
    [BOM_LOAF_ESPTP_R0.ods, BOM_RLHT_R2.ods]
2024-04-29 Updated DCMT pin connections
    [BREAD_Slice.kicad_pcb, BREAD_Slice.kicad_sch]
2024-06-28 Fixed polarity of external power input
    [BREAD_Slice.kicad_pcb]
